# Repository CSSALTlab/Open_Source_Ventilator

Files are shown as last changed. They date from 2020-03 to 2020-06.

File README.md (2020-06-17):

# Open_Source_Ventilator
Open source for use worldwide and contributions from others worldwide

See out documentation at [https://cssaltlab.github.io/Open_Source_Ventilator/](https://cssaltlab.github.io/Open_Source_Ventilator/)

NOTE:
The ventilator code makes references to 2 outside libraries not included in the code found on Github or in the Arduino IDE.

These two libraries are:  

    AllSensors_DLHR (https://github.com/jeremycole/AllSensors_DLHR)
    BMP280 sensor library (https://itbrainpower.net/downloadables/sSense-BMx280.zip)

To add these two libraries to your Arduino IDE:

    Open your Arduino IDE
    Select "Sketch"->"Include Library"->"Add .ZIP library..."
    Navigate to the location of the .zip of the library you downloaded from the websites listed above

Do this for each of the two libraries needed.

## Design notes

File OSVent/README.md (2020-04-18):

# osventproto
OSVent Controller prototype

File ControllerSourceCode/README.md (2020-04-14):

# Controller Source Code Projects

* **ArduinoVent** The final target code for the Ventilator Controller

* **VentSim** The VentSim purpose is to focus on UI and high level control of the Ventilator. Some particular files will be port to the real Ventilator project and others emulates the native Arduino libraries.

### Very first Prototype (before CSSALT PBC)
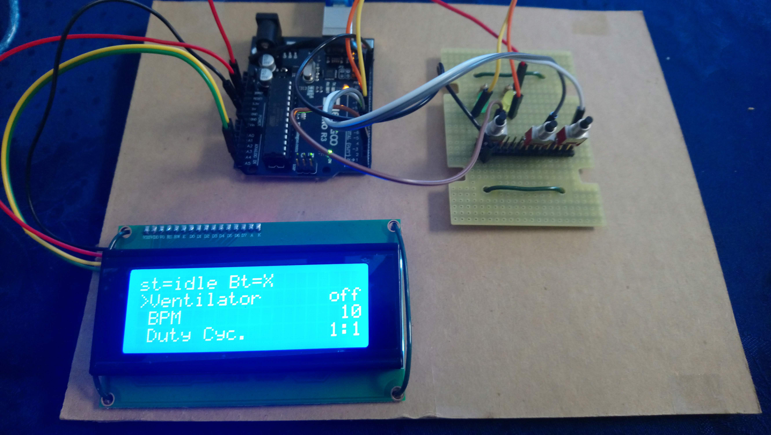
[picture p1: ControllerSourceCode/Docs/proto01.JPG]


### CSSALT PCB Schematic (thanks to Ashhar):
[Click here to see the schematic](Docs/schematic.pdf)

### Demos and Tutorials Videos
[click here for playlist with demo videos and tutorials](https://www.youtube.com/watch?v=gKr-EH8vHxM&list=PLtBsFN3o4c54h5fr7lDnGuZhvKIA5Fhd3)

## Controller
Main function: Provides control for inhalation/exhalation valves and/or stepper motor; monitors pressure and tidal volume. alarms in case of unexpected parameters (unexpected pressure, A/C power down, reset and etc). UI operated by LCD (20x4 20X2 or 16x2) and 3 buttons. Main settings: BPM, duty-cycle, pressure and tidal volume threshoulds.

## UI Options
Whoever is producing the Ventilator can opt to use LCD's: 16X2, 20X2 or 20X4. Interface can be I2C or Parallel. 
## UI Initial concept/proposal

### LCD/Buttons Interface
VentSim simulates the LCD and buttons. The LCD displays the following rows:

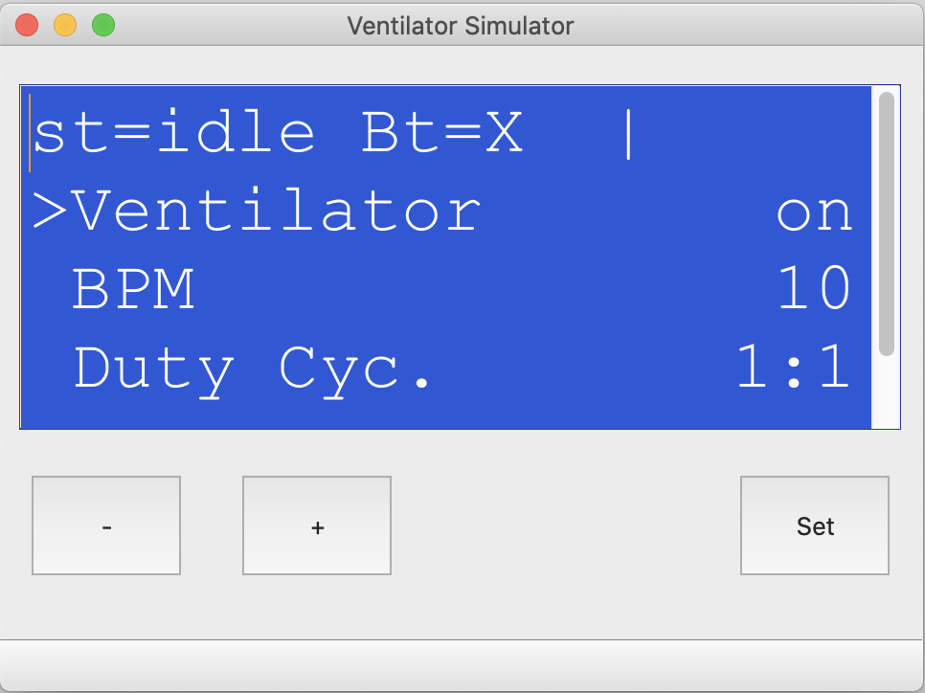
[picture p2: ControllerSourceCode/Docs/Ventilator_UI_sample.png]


Where the rows represent the following tokes:

 * **First Row**: St (Idle, On, or Error). 
   The last 6 characters on the right displays the breath progress, where "||||||" means lung full and 6 spaces empty lung. 

 * **The other rows** are scrollable and show parameters. In "Normal" mode the **"-"** and **"+"** buttons are use to scroll the parameter list. Pressing and hold the **"-"** button scrolls the list up to the top.
 To change a parameter the user needs to press and hold the **"Set"** button for half+ second; it enters in "Enter" mode; then the selected row starts flashing indicating that the parameter can be changed; the The **"-"** and **"+"** buttons increment or decrement the value; Pressing the **"Set"** button commits the change (and so if times-out) and return the unit to "Normal" mode. 

### To Do List
Click [here](TODO.md) to access the TODO list

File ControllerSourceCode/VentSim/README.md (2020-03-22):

# VentSim
The VentSim purpose is to focus on UI and high level control of the Ventilator. Some particular files will be port to the real Ventilator project and others emulates the native Arduino libraries.

## Project concept
The goal of the Ventilator project is to provide ways to anyone produce a ventilator using low cost out-of-shelf components.

### Some suggested components:

* Microcontroller (US$12)
[Amazon link](https://www.amazon.com/Emakefun-Development-Interface-Wireless-ATmega328P/dp/B07RDH8D4T/ref=sxin_0_ac_d_pm?ac_md=1-0-VW5kZXIgJDIw-ac_d_pm&cv_ct_cx=arduino+uno&keywords=arduino+uno&pd_rd_i=B07RDH8D4T&pd_rd_r=054f0126-5538-4fb4-93cc-5a2cf8431b4f&pd_rd_w=xVhNs&pd_rd_wg=rsURv&pf_rd_p=0e223c60-bcf8-4663-98f3-da892fbd4372&pf_rd_r=43RDPGY99Y567EFNAMYY&psc=1&qid=1584833975)
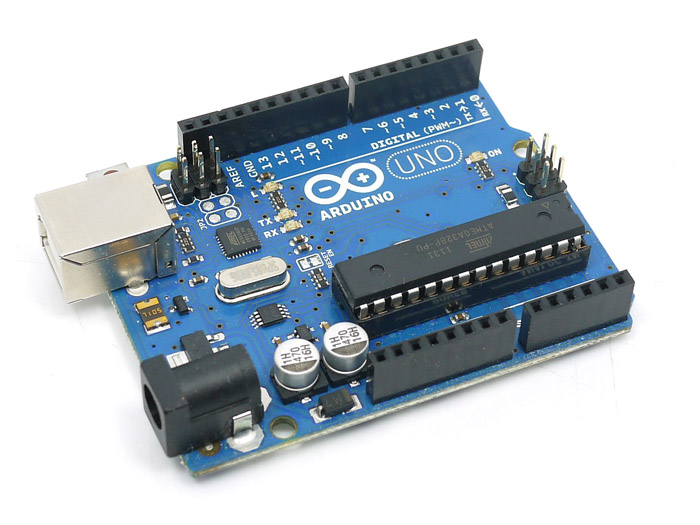
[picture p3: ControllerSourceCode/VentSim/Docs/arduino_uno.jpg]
Arduino


* LCD Module (US$12)
[Amazon link](https://www.amazon.com/ZealMax-Module-Interfaz-Arduino-MEGA2560/dp/B08181VP31/ref=sr_1_fkmr2_1?keywords=arduino+lcd+4+rows&qid=1584834089&sr=8-1-fkmr2)
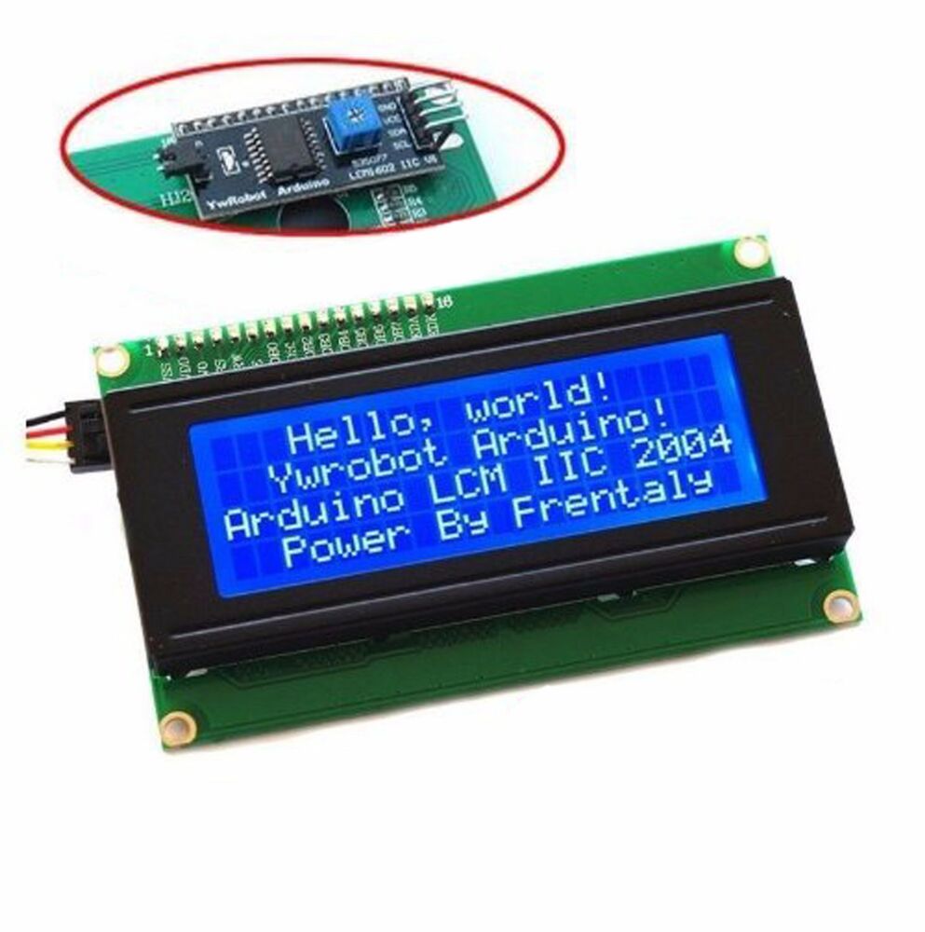
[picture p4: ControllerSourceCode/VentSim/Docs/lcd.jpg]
LCD


* BLE Module - (US$10)
[Amazon link](https://www.amazon.com/DSD-TECH-Bluetooth-iBeacon-Arduino/dp/B06WGZB2N4/ref=redir_mobile_desktop?ie=UTF8&aaxitk=SHdRdFy9Ybn2qMCGps1Sww&hsa_cr_id=8435439580201&ref_=sb_s_sparkle)
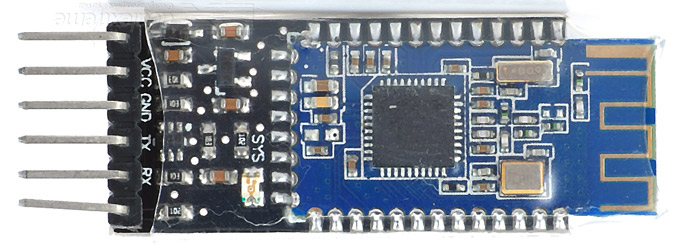
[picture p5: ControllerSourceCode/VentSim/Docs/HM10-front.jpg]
BLE


## Controller
At this point the team building the Ventilator only needs a timer to control breath rate via two valves: inhalation/exhalation valves. Later on we will add a step motor to drive a machanism to squeese a rubber bad/bottle in order to provide positive pressure.

## UI Options
Whoever is producing the Ventilator can opt to use either a LCD + 4 Buttons physical interface or an Android device connected via Bluetooth-LE (according to their budged and components availability). Both option can also coexist fine.

## UI Initial concept/proposal

### LCD/Buttons Interface
VentSim simulates the LCD and buttons. The LCD displays the following rows:

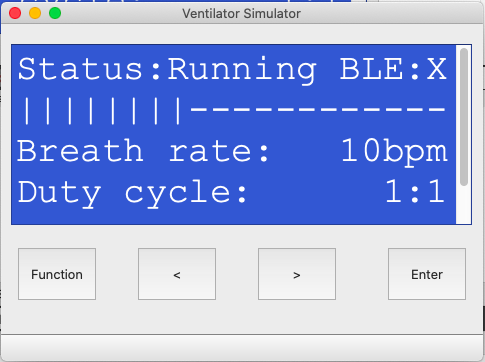
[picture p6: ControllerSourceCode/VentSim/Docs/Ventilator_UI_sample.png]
UI


Where the rows represent the following tokes:

 * **First**: Status (Idle, Alarm/Error or Running). BLE indicates:
   * X: Bluetooth is not installed
   * A: Bluettooth is disabled
   * A: Bluettooth is advertising
   * C: Bluettooth is connected.

 * **Second** row shows in real time the inhalation/exhalation progress.

 * **The other** rows are scrollable and show parameters. The operator can change the parameter values by pressing the Function button. The selected row starts flashing indicating that the parameter can be changed; If Function button is pressed once again then the next row will be selected (flash); if the arrows buttons are pressed then it will increase/decrease the parameter value. The Enter button will commit the change. If Enter button is not pressed (and no other button so) then it will time out and the current parameter will not be changed.

### Android UI
TBD

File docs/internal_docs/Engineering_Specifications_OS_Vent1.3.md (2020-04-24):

**Open Source Ventilator to Address Actual/Predicted Ventilator Shortage Worldwide due to COVID19 Pandemic – Distribute Freely**

V1.3 – Sem Lampotang; March 19, 2020, Department of Anesthesiology, Center for Safety, Simulation &amp; Advanced Learning Technologies, University of Florida, Gainesville, Florida, USA

**Engineering Design Specifications**

**Overall design philosophy**

- Open source for use worldwide and contributions from others worldwide
- Adult ventilator (older adults at higher risk)
- Positive pressure volume control ventilation
- Intubated patient
- A bare bones, safe design is better than nothing and what &quot;nothing&quot; means ….
- The supplies and materials will be locally available at hardware stores
- The design(s) will be validated; validation will be documented and transparent; as an academic research lab, CSSALT can do some of the verification and validation
- The design(s) will be modular allowing different modules to be mixed and matched depending on local availability
- Dissemination via Internet [https://simulation.health.ufl.edu/technology-development/open-source-ventilator-project/](https://simulation.health.ufl.edu/technology-development/open-source-ventilator-project/) and GitHub([https://github.com/CSSALTlab/Open\_Source\_Ventilator.git](https://github.com/CSSALTlab/Open_Source_Ventilator.git))

**Assumptions:**

1. FDA will waive clearance for the bare bones design if there is a massive shortage
2. Traditional medical components and supplies used in ventilators will be in short supply
3. Transportation will be impaired/disrupted. Locally available non-medical supplies and equipment readily available at local hardware stores such as sprinkler valves and PVC tubing will be used

**Ventilator Specifications:**

| | **Range** | **Accuracy** | **Settings** |
| --- | --- | --- | --- |
| **Volume Controlled Intermittent Mechanical Ventilation** |
| Tidal volume | 145-800 ml | ± 20% | Increments of 50 ml |
| Respiratory rate | 10 – 30 bpm | ± 2 bpm | 5 fixed settings: 10, 15, 20, 25, 30 bpm |
| I:E ratio; no inspiratory pause | 1:1 or 1:2 |-| 2 fixed settings |
| PEEP | 0 – 30 cm H2O;Default setting 16 cm H2O | ± 1 cm H2O | Adjustable or fixed settings depending on design |
| Air and O2 supplied at 50 ± 5 psig (345 kPa) |
| FiO2 | 0.21 – 1.0 | ± 0.05 | 3 fixed FiO2 settings: 0.21, 0.5, 1.0 |
| Anti-asphyxia valve | Opens at –3 ± 1 cm H2O |
| Over-Pressure Valve | Opens at 30 cm H2O ± 5 cm H2O |
| **Optional** |
| Spontaneous breathing |
| Weaning |
| In-built blender | 0.5 FiO2 |
| Oxygen sensor | 0.21 – 1.0 FiO2 | ± 0.05 FiO2 |

**Modules:**

Pneumatics

Inspiratory valve

Exhalation valve

PEEP valve

Pressure Regulation (optional)

3D print

Body

Accessories

Electronics

Printed circuit board

Microcontroller

Software or Timing circuit

Power Supply

12V DC preferred

User Interface

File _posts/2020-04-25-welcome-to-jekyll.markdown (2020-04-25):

---
layout: post
title:  "Welcome to Jekyll!"
date:   2020-04-25 01:56:21 -0400
categories: jekyll update
---
You’ll find this post in your `_posts` directory. Go ahead and edit it and re-build the site to see your changes. You can rebuild the site in many different ways, but the most common way is to run `jekyll serve`, which launches a web server and auto-regenerates your site when a file is updated.

Jekyll requires blog post files to be named according to the following format:

`YEAR-MONTH-DAY-title.MARKUP`

Where `YEAR` is a four-digit number, `MONTH` and `DAY` are both two-digit numbers, and `MARKUP` is the file extension representing the format used in the file. After that, include the necessary front matter. Take a look at the source for this post to get an idea about how it works.

Jekyll also offers powerful support for code snippets:

{% highlight ruby %}
def print_hi(name)
  puts "Hi, #{name}"
end
print_hi('Tom')
#=> prints 'Hi, Tom' to STDOUT.
{% endhighlight %}

Check out the [Jekyll docs][jekyll-docs] for more info on how to get the most out of Jekyll. File all bugs/feature requests at [Jekyll’s GitHub repo][jekyll-gh]. If you have questions, you can ask them on [Jekyll Talk][jekyll-talk].

[jekyll-docs]: https://jekyllrb.com/docs/home
[jekyll-gh]:   https://github.com/jekyll/jekyll
[jekyll-talk]: https://talk.jekyllrb.com/

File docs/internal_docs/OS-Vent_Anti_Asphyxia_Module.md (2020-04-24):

**Open Source Ventilator**

**Anti-Asphyxia Module**

V1.0; Sem Lampotang, March 18, 2020; Department of Anesthesiology, Center for Safety, Simulation &amp; Advanced Learning Technologies, University of Florida, Gainesville, Florida, USA

In an intubated patient, the patient will not be able to draw in a breath in periods other than the times during which mechanical inspiration occurs or if the gas supply fails, among others, that is 2/3 of the time if we use an inspiratory to expiratory time ratio of 1:2. An anti-asphyxia valve is a valve that opens when there is sub-ambient (below atmospheric pressure) pressure in the breathing circuit from the patient trying to breathe and not receiving gas. Anti-asphyxia valves typically crack open when the pressure in the breathing circuit is 3 cm H2O below atmospheric pressure. The anti-asphyxia valve module is placed using a T-connection in pneumatic connection with the patient.

| **Physical Input** | **Data/Control Input** | **Physical Output** | **Status** |
| --- | --- | --- | --- |
| **Design** Pressure in breathing circuit | Open the anti-asphyxia valve when breathing circuit pressure drops below -3 ± 1 cm H2O. Accuracy of ± 1 cm H2O | Room air is pulled by the patient via the anti-asphyxia valve as long as the breathing circuit pressure is below – 3 cm H2O Resistance to flow must be minimal. When open, resistance to flow through anti-asphyxia valve must be low (≤ 3 cm H2O/l/s) Design and build/3D print the anti-asphyxia valve and verify it is accurate within ± 1 cm H2O | Not claimed; No one working on it yet |
|
|||| Not claimed; No one working on it yet |

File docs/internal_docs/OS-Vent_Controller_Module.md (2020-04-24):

**Open Source Ventilator**

Controller Module

V1.0; Sem Lampotang, March 17, 2020; Department of Anesthesiology, Center for Safety, Simulation &amp; Advanced Learning Technologies, University of Florida, Gainesville, Florida, USA

This module is essentially a timer that turns two valves on or off. When the inspiratory valve is open, the exhalation valve is closed and vice versa.

Respiratory rate (RR) = Number of breaths per minute (bpm)

Breath duration = 60 s/RR; e.g., for 10 bpm, breath duration = 60/10 = 6 s

Inspiratory:Expiratory time ratio (I:E ratio) = 1:2 (usually)

Inspiratory time (Ti; time in seconds spent in inspiration phase) = breath duration / (1 + I:E) = 6/(1+2) = 6/3 = 2 seconds

Expiratory time (Te; time in seconds spent in exhalation phase) = breath duration – inspiratory time = 6 - 2 = = 4 seconds

Tidal volume (VT) = volume of gas (ml) delivered during inspiration

For a constant flow inspiration, the flow rate to the patient is VT/(inspiratory time)

| **Input** | **Data Output** | **Physical output** | **Status** |
| --- | --- | --- | --- |
| User selects tidal volume (see General Engineering Specifications) || Gas flows towards patient during the selected inspiratory time |
||| In constant flow design, gas flows to patient at a flow rate of VT/ |
 |
| User selects respiratory rate (see General Engineering Specifications) | Time when inspiration starts and ends | Time when gas starts flowing to patient Time when gas stops flowing to patient | Not claimed; No one working on it yet
|| Time when exhalation starts and ends | Time when gas starts flowing from patient Time when gas stops flowing from patient | No one working on it yet ; No one working on it yet |
| **Electromechanical design (no software)** |
| User selects respiratory rate (see General Engineering Specifications) | Time when inspiration starts and ends | 12 V delivered to inspiratory valve 0 V to exhalation valve | No one working on it yet ; No one working on it yet |
|
 | Time when exhalation starts and ends | 12 V delivered to exhalation valve0 V to inspiratory valve | No one working on it yet ; No one working on it yet |
|
| **Electromechanical design (software)** |
| User selection for tidal volume and respiratory rate (see General Engineering Specifications) | Variable &quot;INSPIRATORY\_VALVE\_ON&quot; is true when inspiration starts&quot;INSPIRATORY\_VALVE\_ON&quot; is false when inspiration end | 12 V delivered to inspiratory valve 0 V to exhalation valve | No one working on it yet ; No one working on it yet |
|
 || Variable &quot;EXHALATION\_VALVE\_ON&quot; is true when exhalation starts&quot;EXHALATION\_VALVE\_ON&quot; is false when exhalation ends | 12 V delivered to exhalation valve0 V to inspiratory valve | No one working on it yet ; No one working on it yet |
| **Pneumatic Design – May require specialized parts that may be out of stock** |

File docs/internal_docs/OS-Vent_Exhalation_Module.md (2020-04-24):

**Open Source Ventilator**

**Exhalation Module**

V1.0; Sem Lampotang, March 17, 2020; Department of Anesthesiology, Center for Safety, Simulation &amp; Advanced Learning Technologies, University of Florida, Gainesville, Florida, USA

The exhalation valve is closed when inspiration occurs so that gas from the inspiration module flows to the patient&#39;s lungs. The exhalation valve opens to allow the patient to exhale.

| **Physical Input** | **Data/Control Input** | **Physical Output** | **Status** |
| --- | --- | --- | --- |
| **Design A (balloon exhalation valve with solenoid-activated pilot valve)** |
 Exhaled gas from patient | Time exhalation valve should be open Time exhalation should be closed | Exhaled gas from patient. Inlet and outlet to exhalation module must accept 22 mm corrugated hose used in breathing circuit. When open, resistance to flow through exhalation valve must be low (≤ 3 cm H2O/l/s) | Not claimed; No one working on it yet |
|
| **Design B (exhalation valve with solenoid-activated gate or disc)**
Exhaled gas from patient | Time exhalation valve should be open Time exhalation should be closed | Exhaled gas from patient | Inlet and outlet to exhalation module must accept 22 mm corrugated hose used in breathing circuit When open, resistance to flow through exhalation valve must be low (≤ 3 cm H2O/l/s) | Not claimed; No one working on it yet |
| **Other?** |

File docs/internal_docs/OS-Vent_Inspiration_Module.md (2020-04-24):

**Open Source Ventilator**

**Inspiration Module**

V1.0; Sem Lampotang, March 17, 2020; Department of Anesthesiology, Center for Safety, Simulation &amp; Advanced Learning Technologies, University of Florida, Gainesville, Florida, USA

The inspiration module delivers gas to the patient during the inspiratory time Ti. The inspiration valve closes during exhalation.

| **Physical Input** | **Data/Control Input** | **Physical Output** | **Status** |
| --- | --- | --- | --- |
| **Design A (100% O2)** Oxygen at 50 ± 5 psig (345± 35 kPa) | Time inspiration should be on Time inspiration should be off | O2 flows towards patient at a given flow rate during the selected inspiratory time to deliver the desired tidal volume In a constant flow inspiration, the flow rate is VT/Ti l/s | Not claimed; No one working on it yet |
|
| **Design B (21%-100% O2)** Oxygen at 50 ± 5 psig (345± 35 kPa)Air at 50 ± 5 psig (345± 35 kPa) | FiO2 level selected by user Time inspiration should be on Time inspiration should be off | Gas at desired FiO2 flows towards patient at a given flow rate during the selected inspiratory time to deliver the desired tidal volume In a constant flow inspiration, the flow rate is VT/Ti l/s |
 |
| **Design C (room air)****Mechanically actuated self-inflating bag (aka &quot;Ambu&quot; bag)** | Time inspiration should be on Time inspiration should be off | Air flows towards patient during the selected inspiratory time to deliver the desired tidal volume | **URLs** |

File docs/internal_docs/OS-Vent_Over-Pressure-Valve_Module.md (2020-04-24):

**Open Source Ventilator**

**Over-Pressure Valve Module**

V1.0; Sem Lampotang, March 18, 2020; Department of Anesthesiology, Center for Safety, Simulation &amp; Advanced Learning Technologies, University of Florida, Gainesville, Florida, USA

In an intubated patient under positive pressure ventilation, a concern is that the breathing circuit pressure for some reason such as mechanical malfunction becomes much too high. An over-pressure valve is a cut-off that opens to release gas and therefore reduce breathing circuit pressure if the exceeds a threshold pressure limit. Over-pressure valve valves typically open when the pressure in the breathing circuit exceeds 60 cm H2O above atmospheric pressure. The design could have an adjustable (optional) over-pressure threshold with a default setting of 60 cm H2O. The over-pressure valve module is placed using a T-connection in pneumatic connection with the patient.

| **Physical Input** | **Data/Control Input** | **Physical Output** | **Status** |
| --- | --- | --- | --- |
| **Design** Pressure in breathing circuit | Open the over-pressure valve when breathing circuit pressure goes above -60 cm H2O ± 5 cm H2O. Accuracy of ± 5 cm H2O | Gas in the breathing circuit is released via the over-pressure valve as long as the breathing circuit pressure is above 60 cm H2O ± 5 cm H2O Resistance to flow must be minimal. When open, resistance to flow through over-pressure valve must be low (≤ 3 cm H2O/l/s) Design and build/3D print the over-pressure valve and verify it is accurate within ± 5 cm H2O | Not claimed; No one working on it yet |
|

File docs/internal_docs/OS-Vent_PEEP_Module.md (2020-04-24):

**Open Source Ventilator**

**PEEP (Positive End Expiratory Pressure) Module**

V1.0; Sem Lampotang, March 17, 2020; Department of Anesthesiology, Center for Safety, Simulation &amp; Advanced Learning Technologies, University of Florida, Gainesville, Florida, USA

Reports from our clinical colleagues treating COVID19 patients indicate that PEEP is needed. A patient usually exhales to atmospheric pressure during positive pressure ventilation. Positive pressure means pressure above atmospheric pressure. Simply put, a PEEP valve stops the flow of exhaled gas when the pressure at the end of expiration is at the desired positive pressure.

| **Physical Input** | **Data/Control Input** | **Physical Output** | **Status** |
| --- | --- | --- | --- |
| **Design A (water column)** Gas exhaled by the patient coming from the exhalation valve | Close the PEEP valve when pressure drops below PEEP. Place the end of a 22 mm hose x cm below a translucent plastic cylinder of water with cm markings on the side of the cylinder | Gas exhaled by the patient as long as pressure is above the PEEP level The depth x in cm of the hose end below the water should be the PEEP level in cm H2O Design and build/3D print the PEEP column and verify it is accurate within ±1 cm H2O | Not claimed; No one working on it yet |
|
| **Design B (Spring-loaded valve)** Gas exhaled by the patient coming from the exhalation valve | Inlet port to PEEP valve is 22 mm corrugated hose Close the PEEP valve when pressure drops below PEEP | Gas exhaled by the patient as long as pressure is above the PEEP level Discrete PEEP valves for each PEEP level based on spring tension or an adjustable spring tension for different PEEP levels Design and build/3D print the PEEP column and verify it is accurate within 1 cm H2O | Not claimed; No one working on it yet |

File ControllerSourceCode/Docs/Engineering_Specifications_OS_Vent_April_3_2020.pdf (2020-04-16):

Open Source Ventilator to Address Actual/Predicted Ventilator Shortage Worldwide due to COVID19 Pandemic – Distribute Freely

V1.6 – Sem Lampotang, Dave Lizdas, Tony Destephens, Ilana Zarour; April 3, 2020, Department of Anesthesiology, Center for Safety, Simulation & Advanced Learning Technologies, University of Florida, Gainesville, Florida, USA

Engineering Design Specifications (preliminary and subject to change as needed to meet end-user needs)

Overall design philosophy

- Open source for use worldwide and contributions from others worldwide
- Adult ventilator (older adults at higher risk)
- Positive pressure volume control ventilation for intubated patients who are not spontaneously breathing
- A bare bones, safe design is better than nothing and what “nothing” means ….
- The design(s) will be validated; validation will be documented and transparent; as an academic research lab, CSSALT can do some of the verification and validation
- The design(s) will be modular allowing different modules to be mixed and matched depending on local availability
- Unboxed design – all parts directly accessible
- Design will be inexpensive to build (parts for base model less than $300 US) and assembled quickly (less than TBD hours) with readily accessible parts
- Dissemination via Internet https://simulation.health.ufl.edu/technology-development/open-source-ventilator-project/ (https://simulation.health.ufl.edu/technology-development/open-source-ventilator-project/) and GitHub(https://github.com/CSSALTlab/Open_Source_Ventilator.git)

Assumptions:

1. FDA will waive clearance for the bare bones design if there is a massive shortage
2. Traditional medical components and supplies used in ventilators will be in short supply
3. Transportation will be impaired/disrupted. Locally available non-medical supplies and equipment readily available at local hardware stores such as sprinkler valves and PVC tubing will be used

Ventilator Specifications:

| Range | Accuracy | Settings
Volume Controlled Intermittent Mechanical Ventilation
Tidal volume (TV) | 250-800 ml | ± 25 ml | Increments of 50 ml
Respiratory rate (RR) | 10 – 30 bpm | ± 0.5 bpm | Increments of 2
I:E ratio | 1:1 or 1:2 (1:3 optional) | - | 2 fixed and 1 optional setting
PEEP valve | 5 – 25 cm H2O; Default setting 5 cm H2O | ± 1 cm H2O | Can either be adjustable in 5 cmH2O increments or continuously adjustable

Air and O2 supplied at 50 ± 5 psig (345 kPa)

FiO2 | 0.21 or 1.0
Anti-asphyxia valve | Opens at –3 cmH2O | ± 1 cm H2O
Over-Pressure Valve | Opens at 40 default, adjust up to 60- cmH2O | ± 5 cm H2O | Manually controlled

Optional
Plateau pressure | Limited to 35 cmH2O | | Controlled in software
Peak pressure | < 2cmH2O + Plateau | | Controlled in software
Inspiratory pause | 25% inspiratory time | -
Spontaneous breathing | | | Ventilation mode
In-built blender | 0.21 – 1.0 FiO2 | ± 0.05 (+/- 5%) | 3 fixed FiO2 settings: 0.21, 0.5, 1.0 Variable between 30% and 100% in 10% steps preferred
Oxygen sensor | 0.21 – 1.0 FiO2 | ± 0.05 FiO2

Sensors (optional – not in base design):

Airway pressure sensor

- Connected at 22mm inspiratory port connection
- Capable of measurement ranges of -20 cmH2O to 60 cmH2O (rated for 120 cmH2O over-pressurization)
- at least 1.0 cmH2O resolution
- Used for:
- disconnect and overpressure alarms
- displaying PEEP, peak and plateau airway pressure with waveform (waveform optional)
- aborting inspiration if High inspiratory airway pressure reached

Flow Sensor

- Connected at expiratory port
- Capable of measurement during maximum conditions: max TV 800 ml, RR 30, IE 1:2
- Max flowrate at least 1200 mL/s (72 LPM)
- Accuracy +/- 40 mL/s
- Max flow resistance 2.2 cmH2O at 60 LPM
- Used for:
- Measuring TV via integration over time (measured TV accurate to +/- 25 ml nominal, ideally +/- 10 ml)
- Low/High TV alarms
- Must be able to withstand airway pressures (rated for 120 cmH2O over-pressurization)

User Interface:

− Display
- 20x4 LCD display or equivalent for base design, non-base design supports touchscreen
- Capable of continuously displaying:
User settings for TV, RR, I:E
Ventilator output for TV, PEEP, airway pressure (Paw)
Optional (FiO2, ventilation mode, EtCO2, ventilator output for RR) Alarms
− Adjustable variables
- RR,
- I:E,
- TV,
- Alarm limits

Alarms:

− Patient Disconnect
- Condition: pressure does not rise above 3 cmH2O during inspiration
- Audible alarm and UI text “LOW AIRWAY PRESSURE” [16 Char: LOW AIRWAY PRES! (16 characters)] − High inspiratory airway pressure
- Condition: airway pressure above alarm setting during inspiration
- Adjustable range: 15- 60 cmH2O, increments of 5 cmH2O
- Default setting: 35 cmH2O
- Audible alarm and UI text “OVER-PRESSURE ALARM” [16 char: OVER PRES ALARM! (16 characters)]
- Controller feedback:
Inspiratory solenoid valve closes to stop inspiratory flow Exhalation valve opens (if controlled by solenoid)
− TV High/Low
- Adjustable range: 200-1000 ml, increments of 50 ml
- Default low alarm setting: 200 ml; Default high alarm setting: 1000 ml
- Audible alarm and UI text:
“TV HIGH” Condition: measured TV exceeds high TV alarm setting
“SET TV NOT DELIVERED” Condition: measured TV less than low TV alarm setting [16 Char: SET TV NOT DELIV]
“LOW VT, IT SHORTENED” Condition: Inspiration Time (IT) is shortened by reaching high inspiratory airway pressure limit and measured TV less than low TV alarm setting [16 Char: LOW VT/IT SHORT]
− MV (Minute ventilation) High/Low (Optional):
- Adjustable range: 2 L- 15 L, increments of 1 L
- Default low setting: 4 L; Default high setting: 8 L
- "MV HIGH” Condition: MV greater than high MV alarm setting
- “MV LOW” Condition: MV less than low MV alarm setting
− Gas pipeline failure (Optional)

- Condition: no supply pressure detected
- Audible alarm and UI text “GAS SUPPLY FAILURE” [16 Char: GAS SUPPLY FAIL! (16 char)] − Electricity supply failure (Optional)
- Condition: ventilator unplugged from wall mains
- Audible alarm and UI text “ELECTRIC SUPPLY FAIL” [16 Char: ELECT SUPP FAIL! (16 char)]
− Machine switched off when in mandatory ventilation mode ("Rapidly manufactured ventilator system specification", 2020)
- 16 Char: "VENT TURNED OFF!"
− If multiple alarms simultaneously present and display has one line of text for alarms, display line will toggle through all alarms at one second intervals

Incoming gas supply:

− Must connect to wall pipeline or gas blender
- Male Oxygen DISS connector (from hose)
− (Optional) All gas connectors and hoses must use standard non-interchangeable connectors and be color coded according to current standards ("Rapidly manufactured ventilator system specification", 2020).
- (Optional) Can incorporate a backup oxygen cylinder connected via either Schrader valve or Pin Index System ("Rapidly manufactured ventilator system specification", 2020).

Electrical supply:

− Ability to connect to 120-240V mains
− Must have 30 minutes backup battery in case of mains electricity failure
− Optionally hot swappable batteries so that it can be run on battery supply for an extended period, for example, 2 hours for within hospital transfer ("Rapidly manufactured ventilator system specification", 2020).
− Must avoid harmful RF or EM emissions that could interfere with other critical machinery ("Rapidly manufactured ventilator system specification", 2020).

Gas supply to patient:

Patient breathing system connections- the ventilator must present 22mm outside diameter (OD) ‘male’ standard connectors for connection to user supplied 22mm ‘female’ connectors on the breathing system ("Rapidly manufactured ventilator system specification", 2020).

All elements in the gas pathway must meet biological safety and oxygen safety standards, especially to minimize risk of fire or contamination of the patient’s airway ("Rapidly manufactured ventilator system specification", 2020).

Infection Control:

− All parts in contact with pathogens must be either disposable or able to be decontaminated between patients ("Rapidly manufactured ventilator system specification", 2020).
− All external surfaces must be cleanable in the likely event that they get respiratory secretions or blood splatter on them. Cleaning would be by healthcare workers manually wiping using an approved surface wipe with disinfectant or cloths and approved surface cleaning liquid ("Rapidly manufactured ventilator system specification", 2020).
− Ability to add in line, replaceable HEPA and HME filters to inspiratory circuit.

Miscellaneous:

− Exhalation valve flow resistance: no more than 1.5 cmH2O at 60LPM gas flow
− Over-Pressure Valve flow resistance: no more than 1.5 cmH2O at 60LPM gas flow
− Anti-asphyxia valve flow resistance: no more than 1.5 cmH2O at 60LPM gas flow
− Must be able to deliver 800ml TV 30BPM I:E 1:2 at a constant flow throughout entire inspiration cycle
− It must have 100% duty cycle (100% up time) for up to 14 days. Optionally it can be used beyond 14 days, the expected durability must be specified ("Rapidly manufactured ventilator system specification", 2020).
− Can be floor standing ("Rapidly manufactured ventilator system specification", 2020).
− Ideally small and light enough to mount on patient bed and orientation-independent functioning ("Rapidly manufactured ventilator system specification", 2020).
− Should be as robust as possible. For example, it may be dropped from bed height to floor ("Rapidly manufactured ventilator system specification", 2020).
− It must be intuitive to use for qualified medical personnel, but these may not be specialists in ventilator use ("Rapidly manufactured ventilator system specification", 2020):
- must not require more than 30 minutes training for a doctor with some experience of ventilator use ("Rapidly manufactured ventilator system specification", 2020)
- Must include instructions for use ("Rapidly manufactured ventilator system specification", 2020)
- Must have transparent design, supply chain, manufacture and testing processes that are of sufficient quality to enable regulatory officials to deem appropriate for usage in exceptional circumstances ("Rapidly manufactured ventilator system specification", 2020).
− Must not be excessively cumbersome so that it would impede hospital operations or prevent easy movement within hospital premises ("Rapidly manufactured ventilator system specification", 2020).
− Avoidance of hot spots (overheating components).

References:

Rapidly manufactured ventilator system specification. (2020, March 20). Retrieved March 24, 2020, from https://www.gov.uk/government/publications/coronavirus-covid-19-ventilator-supply-specification/rapidly-manufactured-ventilator-system-specification

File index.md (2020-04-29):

---
layout: default
title: Home
---
# About page

This page tells you a little bit about me.

This is the Open Source Ventilator Project from the University of Forida.

[Operator's manual](./docs/OperatorsManual/manual.md)

[Aeesmbly Instructions](./docs/electronics/assembly_instructions.html)

[version 1.0 testing report](./docs/tests/test_v1.html)

[version 1.09 testing report](./docs/tests/test_v109.html)

Developers:

  [Guide to adding / editing documentation](./docs/AddingDocumentation.md)

  [Guide to developing / testing](./docs/testing/developing_guide.html)

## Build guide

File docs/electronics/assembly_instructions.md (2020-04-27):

# Assembly Instructions
DRAFT V1.
Gordon L. Gibby MD KX4Z
Address questions to docvacuumtubes@gmail.com

|DATE| VERSION| Changes|
|---|---|---|
|4/15/20| Draft 1.0| Original Document|
|4/20/20| Draft 1.1 |Utilized Ashhar 1.0 Board|
|||Added wooden standoffs glued to Ashhar 1.0 Board|
|||Allows use of 4x20 display, but compatible with 2x16 code;|
|||with a different cut-out will accmodoate 2x16 display as well.|
|||Mounted Transducer board to front panel instead of to rear of main board|
|||Provided a Drill Template and dimensions.|
|||Provided a working list of TOOLS REQUIRED|
|4/20/20| Draft 1.2 |Added missing photo of the tools required.|
|4/21/20| Draft 1.3| Added wiring information for I2C bus connections to Transducer board|
|4/23/20| Draft 1.4| Details on final build of Prototype #2|
|4/24/20| Draft 1.5| Added overview wiring diagram|
|||Added R-numbers to Schematic, added missing R10 to list.|
|||Rewrote bill of materials for the electrical construction of the transducer board.|
|||Rescanned the schematic to improve quality.|
|||Listed “missing” resistors (not used)|

## Partial Mechanical Bill of Materials

|# |Item Description| Item sourcing suggested|
|--|--|--|
|1| Carlon 8”x8”x4” electrical box|Home Depot or equivalent https://www.homedepot.com/p/Carlon-8-in-x-4-in-PVC-Junction-Box-E989N-CAR/|
|2| Chosen LCD Display| Connection pins must be on the back of the board and must be long enough to properly connect to the socket on the main board.|
|||20x4: https://www.amazon.com/gp/product/B00GZ6GK7A/ref=ppx_yo_dt_b_asin_title_o08_s00?ie=UTF8&psc=|
|||https://www.amazon.com/gp/product/B071W8SW9R/ref=ppx_yo_dt_b_asin_title_o06_s00?ie=UTF8&psc=
|3 |Pushbuttons| https://www.amazon.com/gp/product/B0752RMB7Q/ref=ppx_yo_dt_b_asin_title_o09_s00?ie=UTF8&psc=|
|4| Pine dowels |3/8” outer diameter x 0.90” length, square cuts, pine (soft)Remember to make pilot drills before inserting sheet metal screws.|
|5| Sheet metal screws| #6 x 5/8” to secure the main board standoffs from the front –qty 3 required.|
|6| #16 or #18 stranded wire, both red and black colors required.|Power supply wiring|
|7| #22-#28 stranded wire| To wire the push buttons. Stranded wire from a Cat5 ethernet cable is excellent.|
|8| Solenoid output jack| CB microphone 4-pin secure insulated jack https://www.amazon.com/PIN-PANEL-MOUNT-MICROPHONE-CONNECTOR/dp/B00H579TXU|
|||Pin 1 = MOTOR_A|
|||Pin 2 = MOTOR_B|
|||Pin 3, 4 = GROUND|
|9| Solenoid plug| https://www.amazon.com/4-PIN-CB-MICROPHONE-PLUG/dp/B00H572J3W (CB microphone 4-pin plug)|
|10| Mean Well 15 volt medical grade power supply| https://www.digikey.com/product-detail/en/mean-well-usa-inc/GSM40B15-P1J/1866-2009-ND/|
|11| BMP or BME| Adafruit version:|
|||https://www.amazon.com/Adafruit-BME280-Temperature-Humidity-Pressure/dp/B013W1AJUY (I2C address 0x77 if not jumpers utilized)
|||An alternative Kee-Yee product has been successfully used but requires a different I2C address (0x76)|
|12| Airway tubing connectors| https://www.amazon.com/Swordfish-61120-Vacuum-Connector-Assortment/dp/B07HV8CVZ|
|13| I2C 3.3V differential pressure transducer, 200Pa| https://www.digikey.com/product-detail/en/amphenol-all-sensors-corporation/DLHR-F50D-E1BD-C-NAV8/442-1163-ND/
|14| PCB for I2C 3.3 V differential pressure transducer, 200 Pa|Manufacturer may redesign the Transducer/power supply board, or use standard perfboard for mounting.|
|15| Nylon insulated standoffs with M3 threads, screws and nuts, assorted lengths|Assortment: https://www.amazon.com/gp/product/B01HDR72Q2/ref=ppx_yo_dt_b_search_asin_title?ie=UTF8&psc=
||Barbed plastic airway tubing connectors |https://www.amazon.com/Swordfish-61120-Vacuum-Connector-Assortment/dp/B07HV8CVZ
||Optional Battery| DURA 12-3.3F Duracell 3.3 AGM 12V sealed lead battery.|
||20x4 Standoffs| M3 nylon standoffs 0392” from shoulder to flat side (Mthreaded screw portion is in addition to this size)|
||Transducer board Standoffs| M3 nylon standoffs 0.600” from shoulder to flat side, not including the threaded screw portion.|

### DRILL TEMPLATE (must be printed so that the lines are exactly 1” grid)
This photo would not fit on this page so it is shown at approximately 66% of normal size



#### NOTE FOR AIR PRESSURE CONNECTORS:

|---|---|
|If using small fuel tubing (approx 1/8” ID) the smallest size nipple (1/8”) in the specified vacuum fitting set will work.| Drill 0.160 for the 1/8” barbs from the specified kit|
|If using smaller tubing (e.g. for 2mm brass connectors)| Drill appropriately for the 2mm connectors.|
||If you have these – it is an advantage as the connections to the I2C differential pressure transducer work better with the 2mm tubing.
||If you don’t have them --- then use tubing to make “adapters” of short sections to go from small tubing to large tubing.|
||The final released versio to the hospitals should have 2mm connectors for the flow measurements, but we can fix that later.|

## Actual Assembly Instructions
### Micro Controller and Electrical Cabinet
1. **Use good engineering practice in all steps where there are issues and record any pertinent
discoveries or suggestions for improvement back to the CSSALT Team (Travis Johnson) @ UF.
Please note any errors in dimensions or conflicts and notify additionally
docvacuumtubes@gmail.com**
1. Choose either a common 16x2 or 20x4 LCD display of any desired color, as requested by
customer, without I2C connectors (we are using parallel wiring connections). The 20x4 is preferred.
The photos that follow are for a 20x4 build. See bill of materials above.
1. Choose an Arduino Nano with 328P processor or suitable backwards compatible improved
device with equal or greater RAM / EEPROM. (Program with supplied code from UF CSSALT)
1. Acquire the electrical plastic cabinet. 8”x8”x4” or larger. A suitable box is: Carlon
[https://www.homedepot.com/p/Carlon-8-in-x-4-in-PVC-Junction-Box-E989N-CAR/100404099](https://www.homedepot.com/p/Carlon-8-in-x-4-in-PVC-Junction-Box-E989N-CAR/100404099) (as per
Bill of Materials above)
1. If the customer requests built-in battery backup, procure a DURA 12-3.3F Duracell 3.3 AGM
12V sealed lead battery.

    This battery can be glued with Epoxy glue as follows, and **must be fully charged by an external
    power supply (suggested, Walmart Everstart 3A battery smart maintainer) before delivery** :

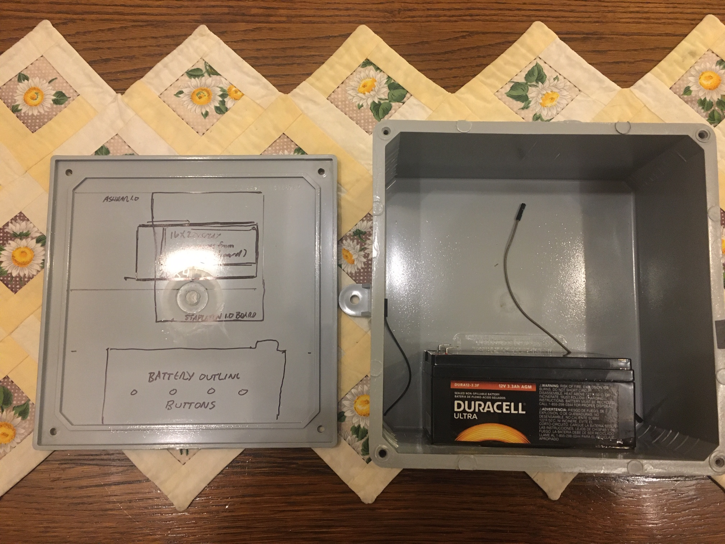
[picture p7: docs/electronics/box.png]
    

1. Assemble the Ashhar Farhan v. 1.0 Board. With the following adjustments:

    |#| Item| Comment|
    |1| BNC or RCA phono jacks NOT REQUIRED |You will likely prefer to utilize #18 or # stranded wire to connect to the “CB 4-pin microphone jack” INSTEAD OF THE BNC OR RCA PHONO JACKS|
    |||Pin 1 = output of MOTOR_A|
    |||Pin 2 = output of MOTOR_B|
    |||Pin3 , 4: GROUND|
    |||Jack body of 4-pin microphone jack – unconnected.|
    |||You may also utilize the appropriate BNC or RCA phono plug if you prefer to install the jacks, and wire to the CB 4-pin microphone jack. This is up to manufacturer preference.|
    |2 |298 Motor controller NOT REQUIRED| Not required. Please do not populate|
    |3| Relays NOT REQUIRED| Not required. Please do not populate|
    |4| Pushbuttons on Board NOT REQUIRED and best not to install | Not required – your assembly will be easier if you do not install them, because you need tosolder stranded wire to your choice of pushbuttons or membrane switches on the front panel.|
    |5| J8 TFT connector| NOT REQUIRED|

1. Orient the Ashhar 1.0 board horizontally well above the battery, note where the chosen display will
be located and **cut an opening for the display** , with approximately <1/16” gap. Later the gap will be
sealed with RTV or caulk. **See Drill Template attached,** and included above. – _print template in
such a magnification that the axes lines are exactly 1.00 inch if you are going to use it as a drill
template. (Note that the board is offset from all interior walls to allow for connectors if utilized )_
1. **_Prepare three pine dowels 3/8” diameter x 0.90” length, with square cuts._** Glue to the board at
the locations specified and be certain that they remain VERTICAL. Suggested to use JBWeld Clear
Epoxy, 5-minute epoxy glue. Place a tiny dab of epoxy on the upper face of the standoffs to harden
them.

    NOTE: that the 20x4 mounting holes do not match the 16x2 holes on the Ashhar 1.0 Board. Your
    board may be slightly different. Make minute changes as needed – the mounting holes for the
    BOARD (pine dowels) and the 20x4 DISPLAY, must agree with each other and depend on the exact
    dimensions of your 20x4 Display WITH THE PINS MATCHING THE PIN HOLES IN THE MAIN
    BOARD. The pins must reach the board pin-sockets when everything is mounted.

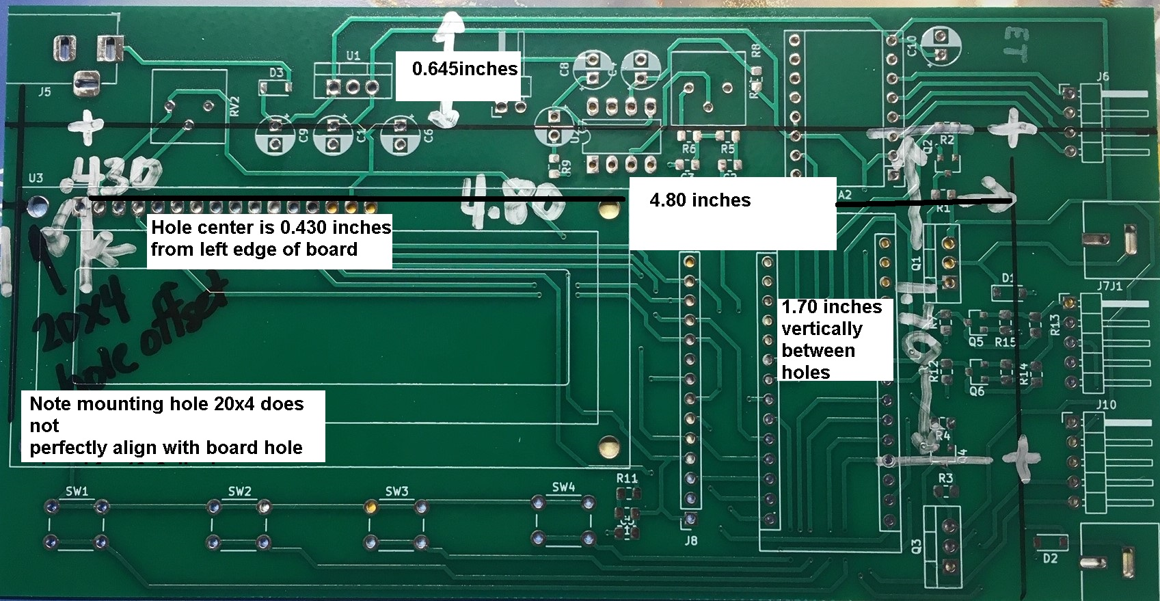
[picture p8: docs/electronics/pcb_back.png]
    

    Drawing of placement of Pin Standoff Dowels.

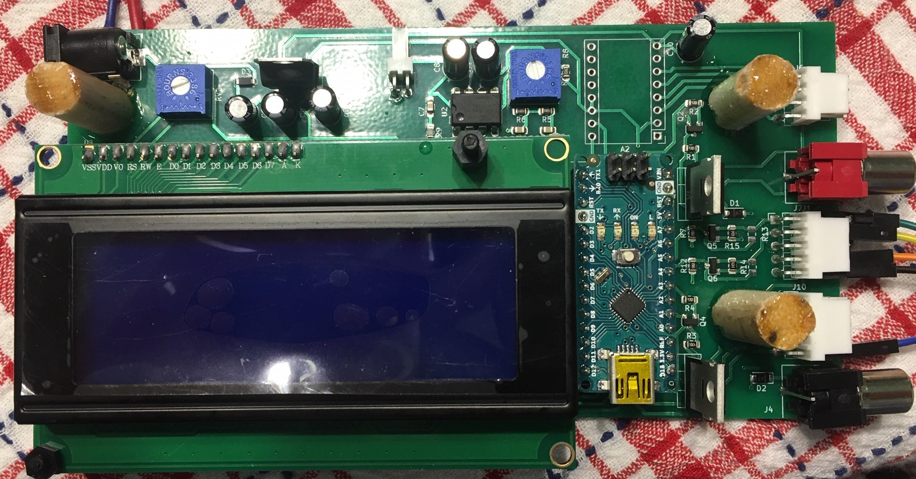
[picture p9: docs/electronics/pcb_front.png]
    

    Photo of example glued pine standoff dowels.

    Cut a hole for the chosen display following the template. It may be useful to use a 3/8” drill inside the
    corners, to allow a sabre saw (jig saw) to make the square cuts. Use a fine-toothed metal-cutting blade
    or equivalent, and go slowly.

    Either use numerically controlled drilling, careful measurements or simply affix the full size Drill
    Template to the inside of the Carlon box cover: (This is best done by spreading 5-minute Epoxy over
    the ENTIRE surface so the entire paper will be affixed and will not rip during drilling procedures.)

    

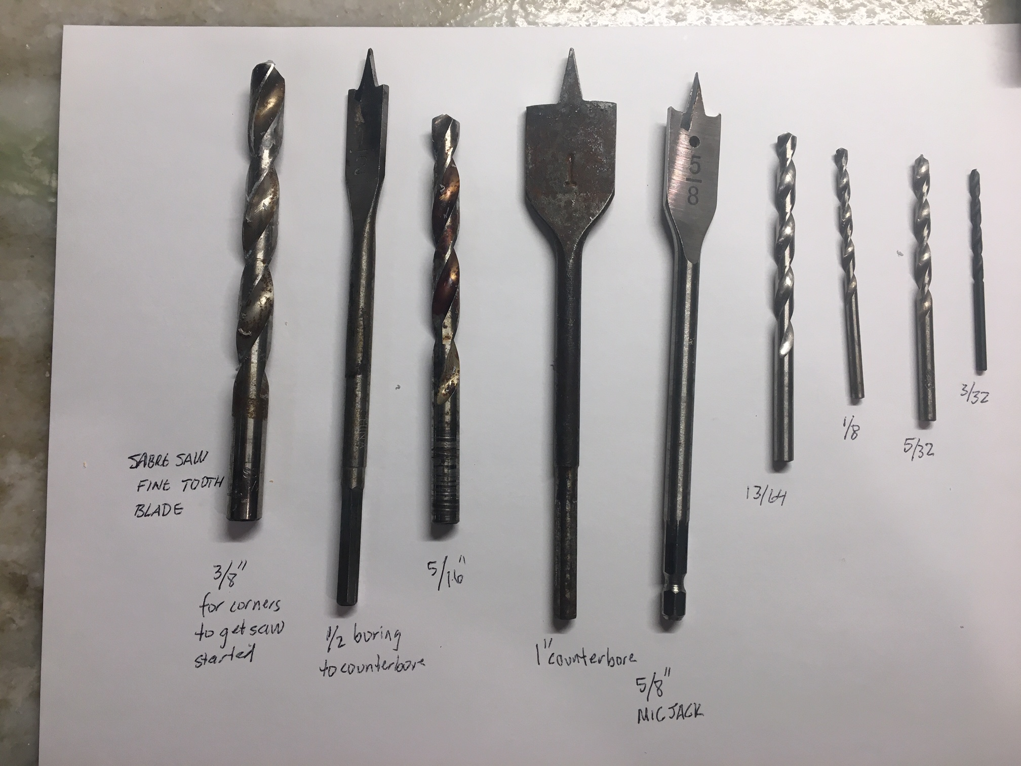
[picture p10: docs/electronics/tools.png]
    

    Photo of all the tools that I used:

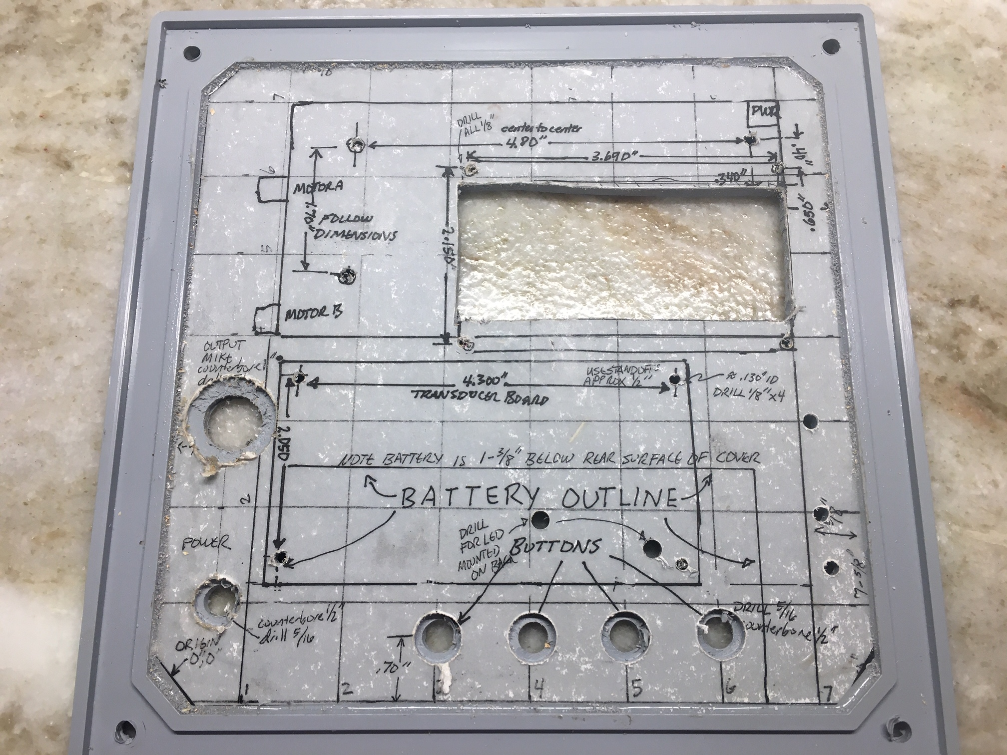
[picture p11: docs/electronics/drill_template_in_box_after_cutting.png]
    

1. Test Fit the chosen display and verify that the holes for its mounting standoffs are properly located – there can be some variation in the displays. Drill for M3 plastic screws using a 1/8” drill bit and
mount the LCD display with 0.392” STANDOFFS chosen such that the Board and Display will MATE
PROPERLY when both are mounted – 0.392” standoffs (not included the threaded screw portion, but
from shoulder to end) work well.

    Mount the 20x4 display; the front edge of the Display will be flush with the INNER surface of the top
    cover. After all is assembled, this gap will need to be filled with RTV.

1. Note that many devices, including many pushbuttons, will need to have a counter-bore of the thick
electric plastic box in order to allow the short threaded portion of the device to have adequate purchase
from its assembly nut to the device. This will apply to the _pushbuttons_ , the female _coaxial power
input_ , and the _4-pin microphone output jack_. The counterbores are done with a flat cutting wood
boring bit, 1/2” and 1” as noted in the drill template.

1. Mount an input power coaxial jack suitable for the plug on the output of the medical grade Mean
Well 15VDC power supply. Wire the coaxial power input jack using #16-#18 stranded wire (red for
positive black for negative) to the “17V” input of the Transducer Board, and to ground on the
transducer board. A 15-volt medical grade MEAN WELL power supply is required, but connects to the
17V input, not the 13.8-16V input. (eg. https://www.digikey.com/product-detail/en/mean-well-usa-inc/
GSM40B15-P1J/1866-2009-ND/7703561 )

    NOTE that the Mean Well medical grade power supply produces 15VDC – but on the transducer board,
    it connects its positive output to the “17V” input. This is purposeful. The resulting output is correct.

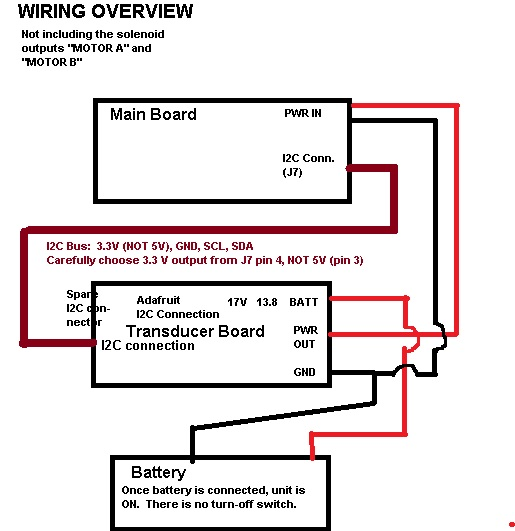
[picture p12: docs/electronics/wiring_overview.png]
    

1. The OUTPUT of the transducer board will need to be connected to the Main Board using #18-#
stranded wire, paying attention to POLARITY (center positive, outer negative) on the input power
coaxial jack. It is difficult to find a male plug to fit into the main board coaxial jack – you may solder
    to the correct solder points on the main board power input jack. Note that the main board includes a
    series diode for polarity protection.

### TRANSDUCER/POWER SUPPLY BOARD: BATTERY

1. If a battery is requested by the customer, wire the battery (positive and ground wires) using
female, insulated, crimp terminals to mate with the battery and #16–#18 stranded wire. Observe
polarity; diodes will prevent the battery from being utilized if it is connected backward, but the trickle
charging circuity may be damaged. Use RED for the positive wire and BLACK for the ground
connection (to MINUS on the battery)
1. **Solder the AC PWR LED ( GREEN ) and ON BATT LED (RED) to the BACK side of the
transducer board** , at an appropriate length so that they enter the holes drilled for them on the top
cover of the box, using the plastic standoffs.
1. Mount the ADAFRUIT BMP/BME280 breakout board (https://www.amazon.com/Adafruit-
BME280-Temperature-Humidity-Pressure/dp/B013W1AJUY or alternate supplier ) to the board with
soldered connections, and glue on the barbed nipple as per demonstration and information from David
Lizdas.

    BMP280 utilize one of the 1/4” x 1/8” adapters, (from a kit such as:
    [https://www.amazon.com/Swordfish-61120-Vacuum-Connector-Assortment/dp/B07HV8CVZ](https://www.amazon.com/Swordfish-61120-Vacuum-Connector-Assortment/dp/B07HV8CVZ)
    ) epoxy glue the 1/4” side AROUND the bmp280 to the board itself, being careful NOT to get
    glue inside on the BMP280 chip.

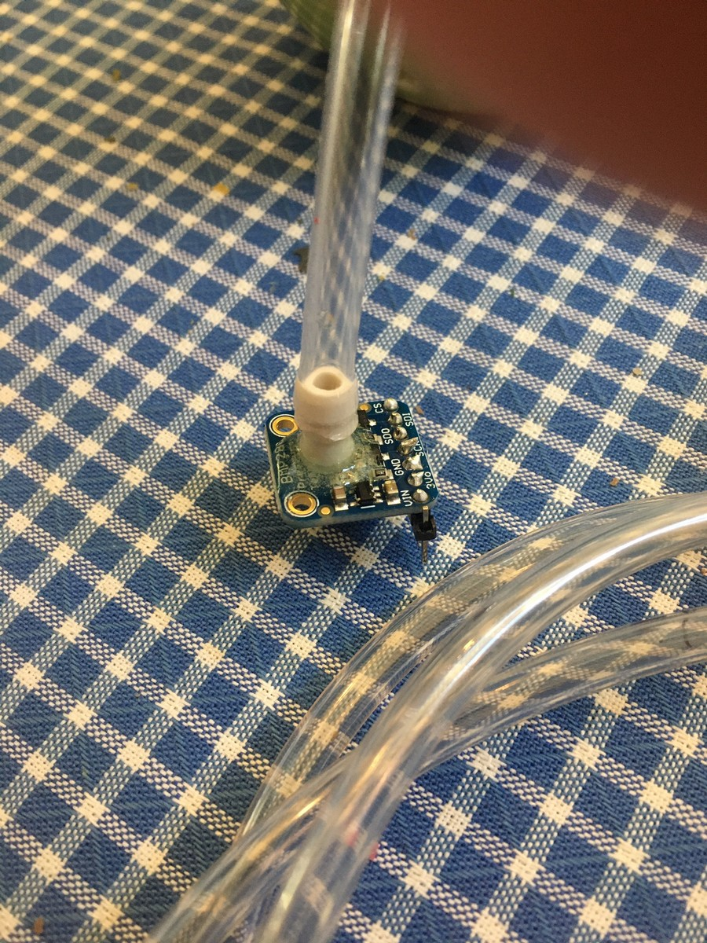
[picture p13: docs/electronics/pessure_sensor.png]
    

    (the 1/4” x 1/8” adapter barb is preferred to allow smaller tubing to be utilized )

1. Wire the chosen differential pressure transducer with a suitable glue onto the board; the traces on
the board **do not match the current choice for the differential pressure transducer, so it must be
individually wired to the ASHHAR 1.0 board using stranded wire (suggest size #22-#32).**

    The differential transducer part specified is: https://www.digikey.com/product-detail/en/amphenol-all-
    sensors-corporation/DLHR-F50D-E1BD-C-NAV8/442-1163-ND/6200354 Note that this is a 3.3 Volt
    maximum device I2C – do NOT connect to 5.0 V. **We unfortunately do not have a printed circuit
    board for this discrete part**. Manufacturer may optionally

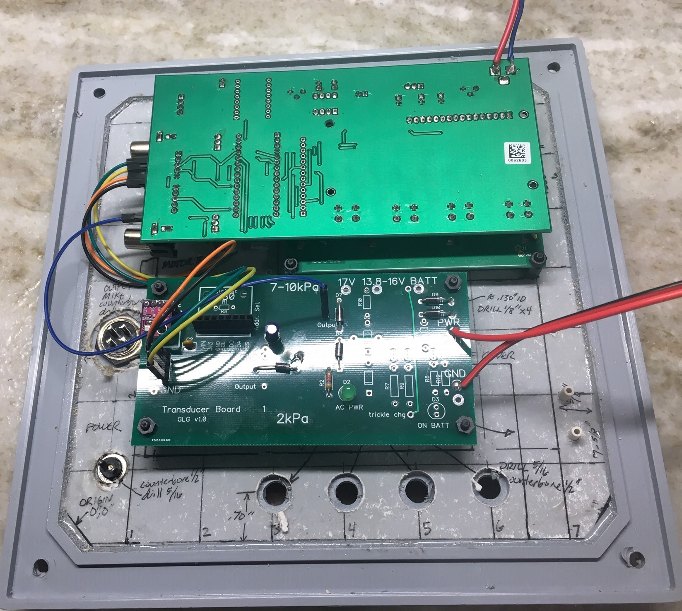
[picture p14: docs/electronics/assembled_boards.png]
    

    a) wire on perfboard and make mechanically stable

    b) Redesign the Transducer/Power supply board to fit this part

    c) Create their own printed circuit board of their own design,

1. Transducer/Power Supply board is mounted on M3 0.60” standoffs at the prescribed location,
taking care so that it will not interfere with the glued battery.
1. The UF Team tasked me on Wednesday April 22 with mounting two plenums for the flow
transducer tubing INSIDE the enclosure. The LifeMech team should skip this on their prototype and
we will provide them exterior to the box. Photo below shows where I placed them. In future builds
we will move the battery off-center so that the plenums can be mounted both on the same side.

    
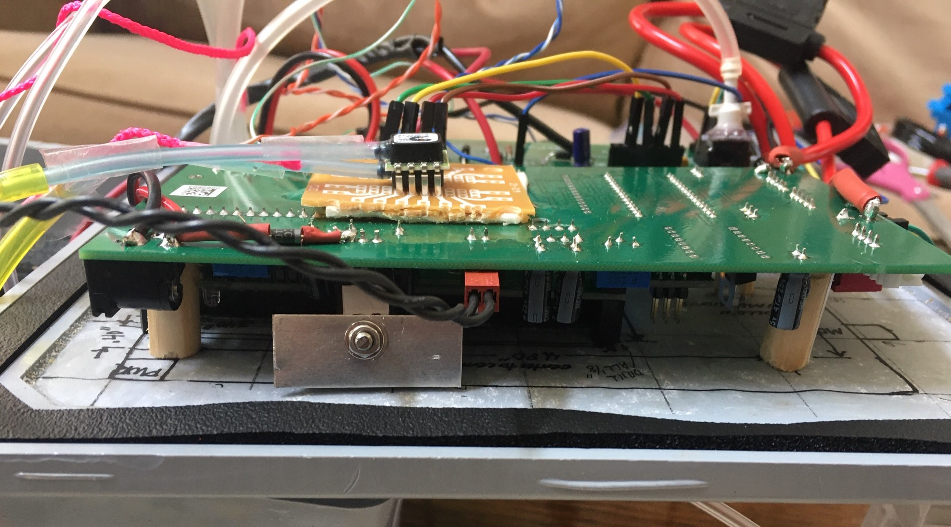
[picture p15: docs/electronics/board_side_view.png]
    

    OPTIONAL home made heatsink on the 5V regulator. Not necessary unless operated in an non-
    airconditioned environment. A small piece of any metal provides additional heat radiating capacity.
    Prevent contact with any other portion of the board as this may be at a voltage potential.

1. Manufacturer may choose to use four push buttons or a 4-switch Normally Open membrane switch
assembly. Mount the chosen pushbuttons and use wiring with very careful soldering to the bring the
four pushbuttons individually in parallel with the onboard connections to the (unnecessary) on board
pushbuttons. #22-#28 stranded wire may be utilized.

1. Output to Solenoids: Mount the output CB MICROPHONE JACK (Part:
https://www.amazon.com/PIN-PANEL-MOUNT-MICROPHONE-CONNECTOR/dp/B00H579TXU )
to the front panel and wire to the ASHHAR BOARD 1.0 as described, either with soldered wires or
with BNC or RCA Phono connectors.

    MOTORA to Pin 1

    MOTOR B to Pin 2

    GROuND to Pin3 and Pin 4

    The final product from commercial manufacturers must have 2 Amp fuse in each solenoid line. In
    this photo you can see that I did the best I could as all I had was #12 gauge fuse assemblies:

    

    NOTE ALSO that I have a (black cable) extension on the USB connector on the Arduino to make it
    easier for me to add and test code. You can REMOVE THIS before clinical delivery.

1. Connector to go to solenoids: 4-pin microphone plug: https://www.amazon.com/4-PIN-CB-
MICROPHONE-PLUG/dp/B00H572J3W Wire with shielded cable with 3 or more stranded
conductors (#16-#22) (example: https://www.homedepot.com/p/Southwire-By-the-Foot-22-4-Gray-
Stranded-CU-CL3R-Shielded-Security-Cable-57572499/204725191 ) with the shield connected to
ground (pins 3 and 4) and pin 1 connected to the INSPIRATORY solenoid and pin 2 connected to the
solenoid driving the EXPIRATORY pneumatically operated valve; the other wire on each solenoid is
connected to ground.

1. Air pressure monitoring: If possible, use 2mm tubing and 2mm brass tubes. If this is not
possible, then: Utilizing standard automobile vacuum tubing fittings such as 1/8” x 1/8” (from:
https://www.amazon.com/Swordfish-61120-Vacuum-Connector-Assortment/dp/B07HV8CVZ8 ) ,
mount and glue-secure barbs through the front panel. Using flexible tubing, connect from the inner
barbs to the

    a) manufactured nipple barb on the BMP (AIRWAY PRESSURE)

    b) upstream and downstream barbs from the ventilator airway components to the barbs on the chosen differential pressure transducer.

    I prefer to have 1/8” barb nipples for connections to small plastic tubing, such as the 1/8” fittings from
    this kit: [https://www.amazon.com/Swordfish-61120-Vacuum-Connector-Assortment/dp/B07HV8CVZ8](https://www.amazon.com/Swordfish-61120-Vacuum-Connector-Assortment/dp/B07HV8CVZ8); but for the BMP280 utilize one of the 1/4” x 1/8” adapters, glue the 1/4” side
    AROUND the bmp280 to the board itself, being careful NOT to get glue inside on the BMP280 chip.

    In the following photos, the tubing from the PATIENT side of the expiratory physical obstruction is
    marked throughout its course with red string:

    

    NOTE: If the flow measurements have the wrong sign, reverse the connections inside the box.

    

21. Provide a 2-3” 16 ohm speaker for the sound output and mount to an internal surface of the box.
22. Be certain that there will be **no mechanical or electrical conflict** when the top is affixed to the
board.

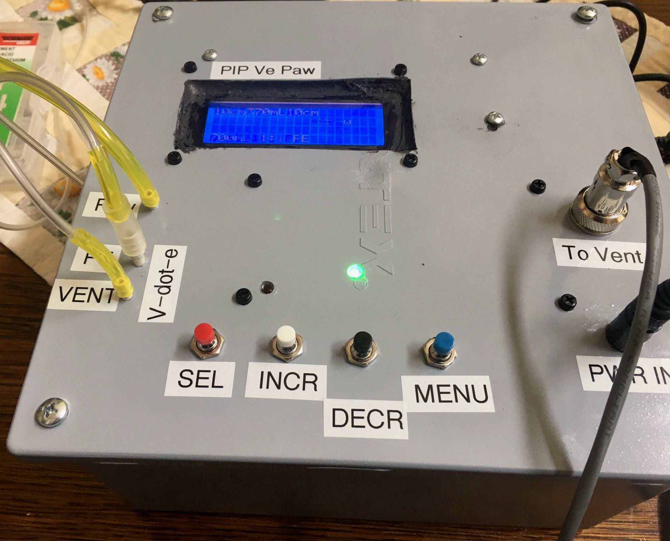
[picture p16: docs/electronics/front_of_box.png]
  

### WIRING UP PERIPHERALS

We have standardized on giving ONLY 3.3VDC to the I2C devices – wire ONLY the 3.3V output from
the board to the V-in terminal of the Transducer board. Depending on what analog transducer you may
be using, you will need to choose what voltage goes to the +5VDC – if you even use U7 or U8. These
are NOT used on the standard FDA submission version from UF

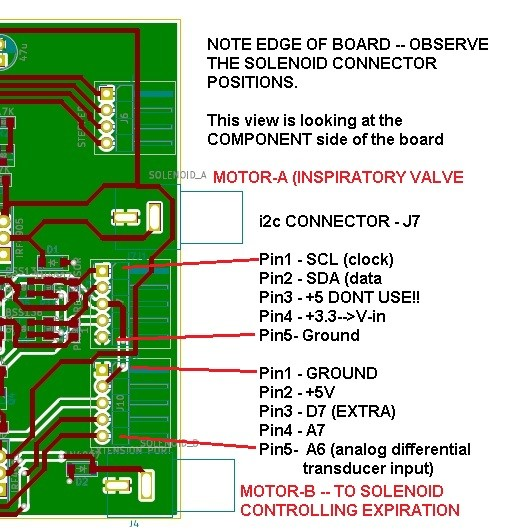
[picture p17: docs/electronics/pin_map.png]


#### WIRING TRANSDUCER BOARD I2C CONNECTIONS

Make the following connections, using either secure pin connectors or soldered wiring:

Main Board J7 Transducer Board Left-Side I2C connector
Pin 1 – SCL (clock)--------------------------SCL
Pin2 – SDA (data)----------------------------SDA
Pin3 DO NOT CONNECT to I2CBus----NO CONNECTION
Pin 4 3.3VDC---------------------------------VIN
Pin5 Ground----------------------------------GND

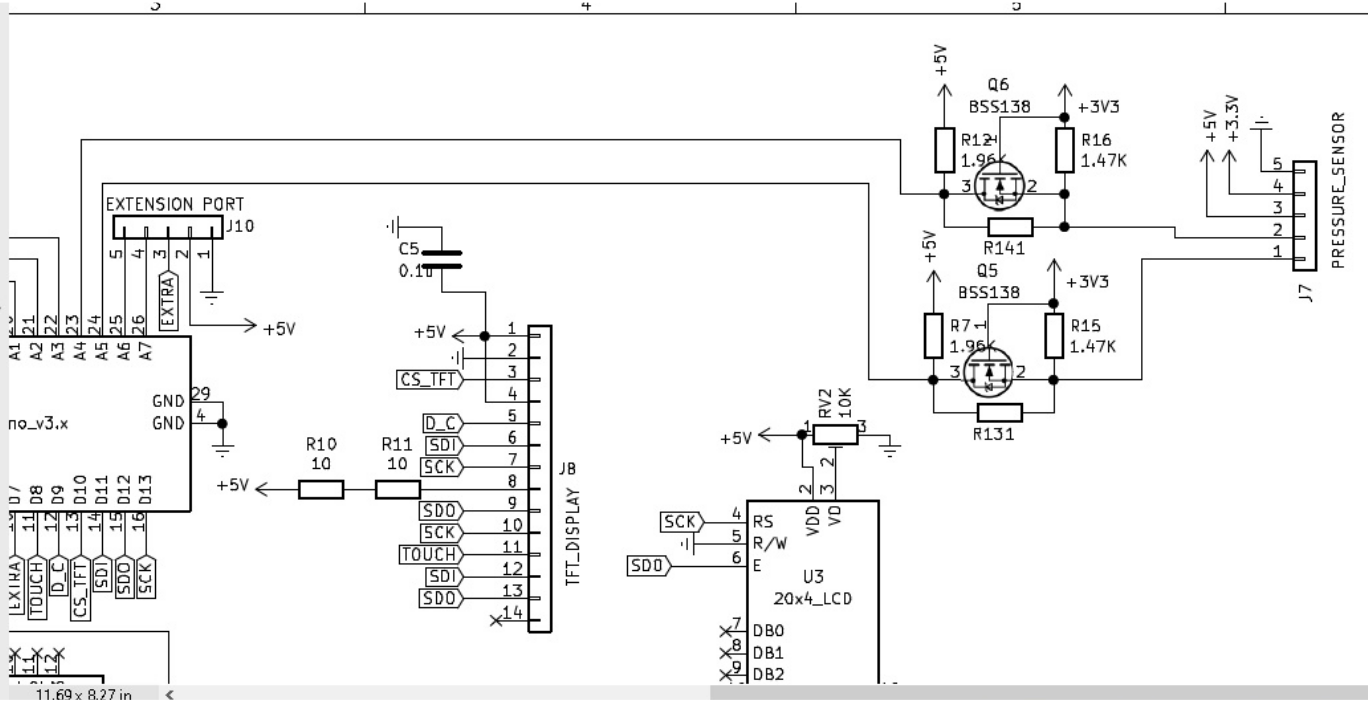
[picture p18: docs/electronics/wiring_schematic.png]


### SOFTWARE SETUP

TODO: Fix this such that pulls from github and installs automatically

Because the code for our project was developed by volunteers literally around the world, most of whom did NOT have access to the same discrete parts, we had to develop with widely varying, but functionally equivalent hardware. As a result it is easiest if you equip your ArduinoIDE as follows:

1. An overview on how to install libraries: [https://www.arduino.cc/en/Guide/Libraries](https://www.arduino.cc/en/Guide/Libraries)
1. Download and install this BMP180 Library: (don’t unzip it);
[https://groups.io/g/VentilatorDevelopers/attachment/1241/0/BMP180MI.zip](https://groups.io/g/VentilatorDevelopers/attachment/1241/0/BMP180MI.zip)

Possible alternates:

[https://bitbucket.org/christandlg/bmp180mi/](https://bitbucket.org/christandlg/bmp180mi/)

A complete set of instructions and another source for that library can be found here (strongly suggest
you read this):

[https://www.ardu-badge.com/BMP180MI/zip](https://www.ardu-badge.com/BMP180MI/zip)

We don’t actually USE this library, but your life will be easier if you just go with the flow here.

1. Download and install the ssense version of the BMP280 library:

[https://create.arduino.cc/projecthub/dragos-iosub/arduino-bme280-sensor-how-to-115560](https://create.arduino.cc/projecthub/dragos-iosub/arduino-bme280-sensor-how-to-115560)

1. SETTINGS that may be of importance to you

|File| Action| Source Code|
|--|--|--|
|Vent.h | Must uncomment the proper one to get the correct code as part of your compile for the flow transducer.|`#define ANALOGDIFFTRANSDUCER // if using the 2kPa analog transdcuer`|
|||`#define I2CDIFFTRANSDUCER // if using the I2C transducer`|
|||
|Vent.h |Get the right display uncommented!!|`#define LCDDISPLAY 2004`|
|||`//extern LiquidCrystal_I2C lcd;`|
|||`//#else`|
|||`//#define LCDDISPLAY 1602`|
|||
|Vent.h |Must uncomment to use the BMP280 (versus BMP180)| `#define USE_BMP280 1 /// set to 0 if not using the BMP280`
|||
|Vent.h |I2C flags of how the bus is working|`#define I2C_BUSY (0x99)`|
|||`#define I2C_READY (0x38)`|
|||
|Vent.h |Where to find the bmp180 library. Trying to root it out of the code is much harder than just loading it...... |`// LIBRARIES`|
|||`// BMP180 https://groups.io/g/VentilatorDevelopers/message/1241`|
|||
|Vent.h |Very important file. You must use the ssense type of BMP280 library.| `#include <sSense-BMx280I2C.h> // Download link halfway down this page:`
|||`//https://create.arduino.cc/projecthub/dragos-iosub/arduino-bme280-sensor-how-to-115560`
|||
|.ino file| Each gives terse explanation. Remember that debug code will take away crucial RAM space and may cause instabilities of the running code so only using temporarily.| `//#define DEBUG // Turn on to debug`|
|||`//#define SHOWINSTANTFLOW // to see calculations of instantaneous flow`
|||`//#define TOTALTIDAL-DISPLAY // to see the tidal volume calculated each breath`
|||`//#define BMP280DEBUG // to see serial port related to BMP`
|||`//#define AIRWAYPRESSURECHECKING // help me figure out why the valve isn't opening`
|||`//#define SERIALPRINT; // gives a load ofprintouts on pressure monitoring`
|||`//#define SMOOTHPRESSURERUN //Investigating expiratory ringing and assist control ventilation`
|||`//#define DIGITALPRESSURESPY // to see measurements related to digital I2C diff press`
||||
|.ino file| Different BMP280’ breakout boards may express different addresses.....beware!| `#define BMP_ADDRESS 0x76 // *****GLG FOR THE KEE-YEE!!!!`|
||||
|.ino file| The uBitx transceiver uses different wiring to the LCD display – be certain that you have the right pins selected if you change hardware. |`//static LiquidCrystal lcd(8, 9, 10, 11,12, 13); //when using ubitx board`|
|||`LiquidCrystal lcd(13,12,11,10,9,8); //when using the GAINESVILLE VENTILATOR`|
|Vent.h| Pin assignments for your hardware MUST be correct or things won’t go as planned.|`#define ALARM_PIN 6`|
|||`#define FN A0`
|||`#define UP A1`
|||`#define DOWN A2`
|||`#define ON_OFF A3`
|||`#define TFT_CS 10`
|||`#define TFT_RS 9`
|||`#define CS_PIN 8`
|||`#define MOTOR_A 2`
|||`#define MOTOR_B 3`
|||
||Defines the number of slices in time the respiratory cycle is set to. I don’t recommend increasing this.|`#define MAX_PHASES 20 //At 40 the machne could barely keep up`

INITIAL Qualification:

1. Apply battery power (if selected) and verify that the RED battery light comes on and the LCD
powers up.
1. Apply power from the 15V medical grade power supply and verify that the GREEN AC power
led comes on.
1. Further function testing will be provided shortly.

APPENDIX Ashhar 1.0 Board

Schematic:

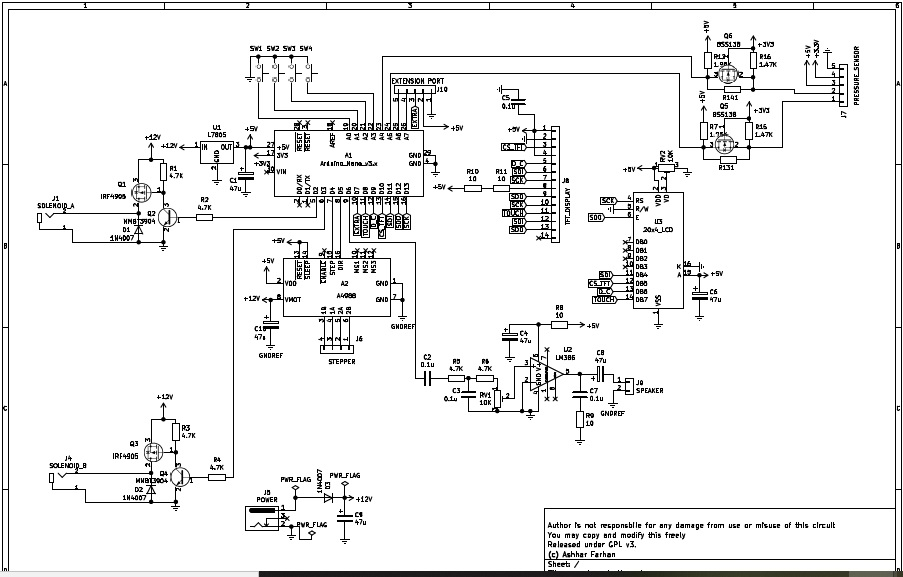
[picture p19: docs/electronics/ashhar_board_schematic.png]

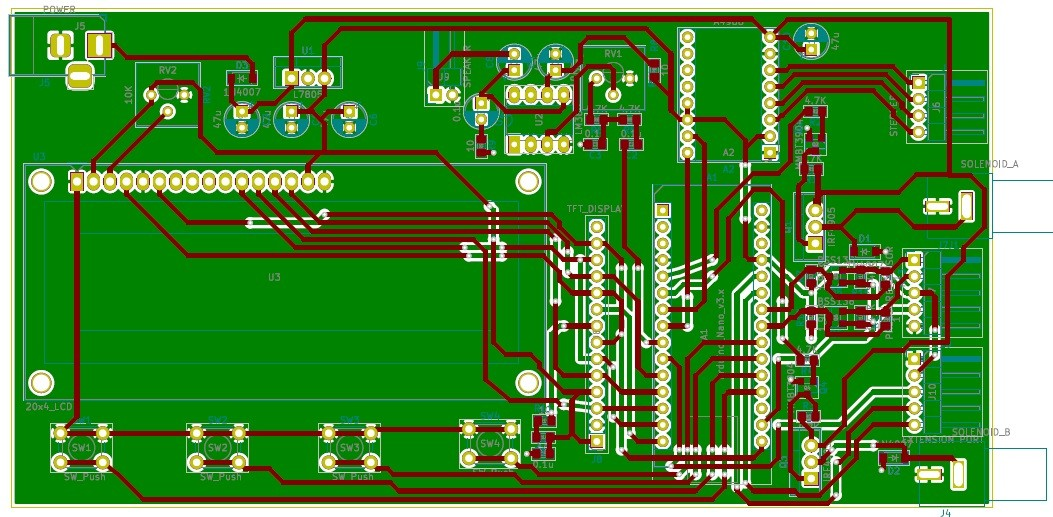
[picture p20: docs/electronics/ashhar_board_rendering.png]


APPENDIX: Schematic for Transducer Board and Parts Values

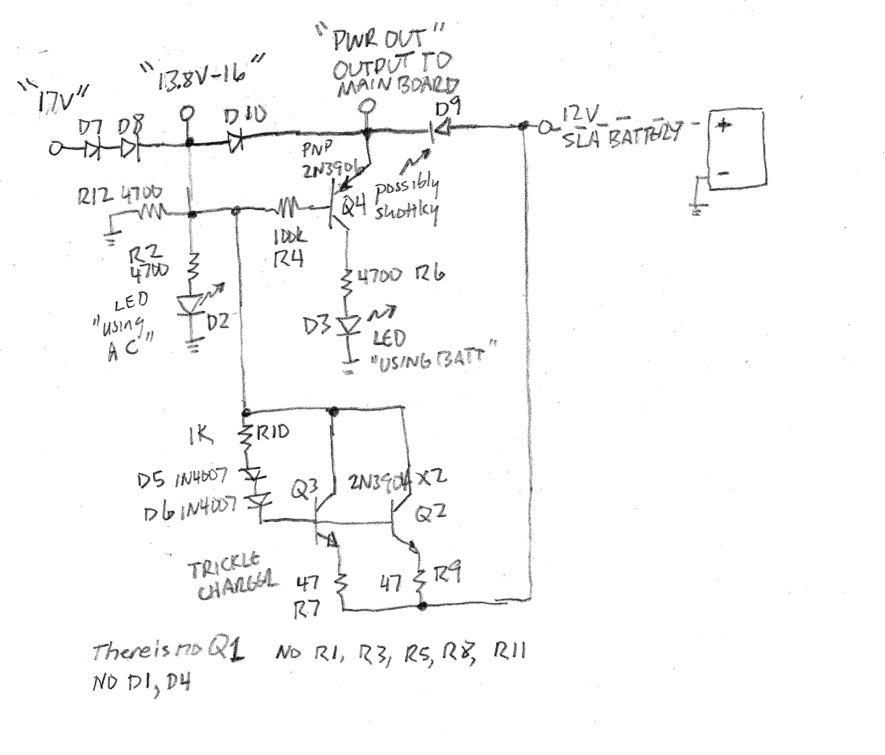
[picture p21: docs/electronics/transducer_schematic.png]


Schematic of “Transducer” Board which includes a Diode-OR connection for two different DC sources,
and a small trickle charger (constant current) for a 12 volt sealed lead acid battery.

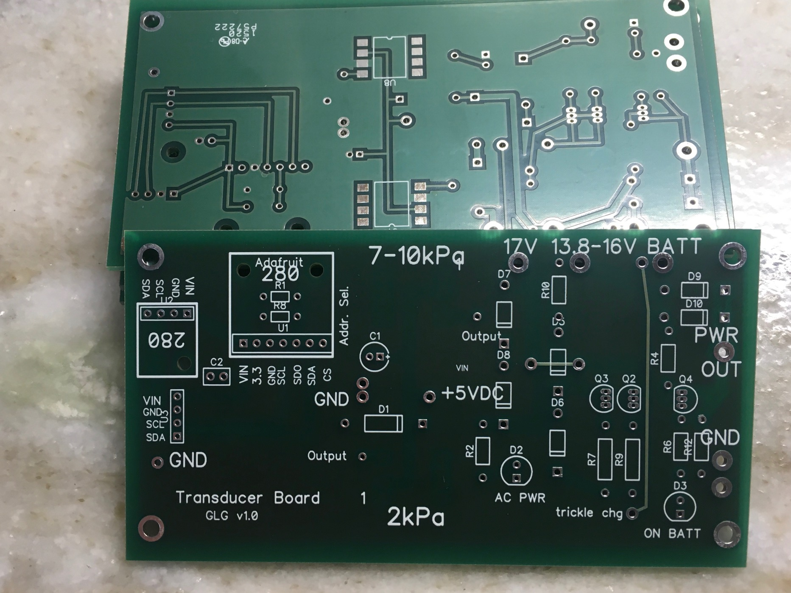
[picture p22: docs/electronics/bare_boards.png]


||Part|Details | Comments|
|--|--|--|--|
||Adafruit 280| Breakout board for Adafruit BMP or BME 280 (either works) R1 and R8 are NOT needed; they are there to change the address from 0x77 if desired.| Although this board is capable of operating at 5V bus voltage, we intentionally operate the bus at 3.3V because many differential pressure transducers require 3.3 V bus and will be damaged by 5V|
||Additonal “280”| This was laid out to fit a certain clone (“Kee-Yee”) of the bmp280 board – optional alternative – not needed and may be used to provide connections to the I2C differential pressure transducer.| There are many different BMP280 breakout boards on the market and they all appear to use **DIFFERENT PINOUTS.** Observe signal names carefully.
||C1| Electrolytic 20-47uf @ >20VDC||
||C2| 0.1V @ >20VDC|
||Input I2C connector| Solder or use 0.1” header as desired|
||ALL RECTIFIER DIODES (D7, D8, D6,D5, D9, D10)| 1N4007 1Amp or equivalent||
||D2 “AC PWR”| Green LED (manufacturer choice of size)|
||D3 “ON BATT”| Red LED (manufacturer choice of size)|
||Q1| none||
||Q2 Q3| 2N3904 NPN transistors||
||Q4| 2N3906 PNP transistor||
|||
||R1| none||
||R2| 4700 ohm 1//4 watt||
||R3| none||
||R4|100K ¼ or 1/8 W|
||R5| none||
||R6| 4700 ohm 1/4W|
||R7| 47 ohm ½ watt||
||R8| none|
||R9| 47 ohm ½ watt||
||R10| 1000 ohm ¼ watt||
||R11| none||
||R12| 4700 ohm 1/4W||

APPENDIX: Suggested Important FMEA topics

Assumptions: Single failures
Other input values normal.

|Function|Faliure|Cause|How weworked to show it.|
|--|--|--|--|
|Move medical gases in and out of the patient in the right amount, the right pressure, and the right timing.| Wrong gas.| Hospital line failure We can’t. |External to our device|
||Wrong mix %| Blender failure| Require external oxygen monitor.|
||Too much inspiration.| Regulator failure| Auto release of pressure if limit exceeded, auto opening of expiratory valve. High volume alarm. |
|| Too much inspiration| Patient compliance improves| High Vol alarm signals to clinician
|| Too much inspiration| Pressure sampling line gets plugged meaning we can no longer measure pressures| Alarm, either low or high pressure, and alarms, high flow.|
||Too much inspiration| Software hang| Watchdog timer will release software and reset and pause and rezero.|
||Too much inspiration| Timing failure| Extraordinarily unlikely if device passes initial quality testing. There are NO blocking calls in the software.|
|| Too little inspiration| Mechanical regulator failure| Low Vol and Low flow alarms.|
||Too little inspiration| Breathing circuit disconnection| Low Vol and Low flow alarms.|
||Too little inspiration| Plugged ETT| High pressure alarm and low volume alarm will sound.|
||Too little inspiration| Faulty flow measurement| Clinician observation of the patient as a confirmation of unusual reported values. Also blood gases.|
||Too little inspiration| Software failure “hang”| Extremely unlikelyl after long term testing of software; requires non-repeatability of code or memory leak, which would be unlikely not to show witihn a thousand cycles.|
||||Watchdog timer will reset the entire processor.|
||Too little inspiration| I2C bus failure| We designed a complete sysetm to deal properly with this extremely rare pheomenon and to continue to ventilate in an open loop manner as previously programmed.|
||Too high a pressure| Patient or ETT condition| Automatic release of pressure by both closing inspiratory valve and opening expiratory valve. High Pressure alarm.
||Too high a pressure| Clinician mis-setting| Automatic release of pressure above set limit and High pressure alarm|
||Too low a pressure| Disconnection |Low Pressure and low flow alarms.|
||Too low a pressure| Misconnection with gas flow diverted through a leak| While an obstructed leak (into bedclothes) might fool the low pressure alarm, because we measure flow in the EXPIRATORy limb, the low volume will be detected.|
||Too LONG inspiratory effort| Clinician missetting| Limits on I:e and respiratory rate make this very unlikely
||To Short inspiratory effort | Clinician missetting| Limits on I:E and respiratory rate make this very unlikely|
||Failure of ventilation system | Improper voltage from mains, resulting in damaged power supply and failure | Medical grade power supply is function from well below normal mains to well above european mains votages. Battery backup will pick up the supply and indicate the failure with a red LED. Failure of pressure monitiring or flow monitoring system.|
||Faliure of pressure monitoring or flow monitoring system | Failure of I2C buss| Solder connections; operate system at 3.3VDC; carefully developed watchdog system will kick in and provide open loop ventilation of the patient.|
||||
|Physically connect to the patient breathing circuit| Improperly fitting airway connectors. || We use industry standard sizes, so very unikely. Having pre-use checkout by clnical users should detect it

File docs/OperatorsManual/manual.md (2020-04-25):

---
layout: default
title: Operator's Manual
---

PanVent User Manual

| **Version** | **Date** | **Who** | **Comments** |
| --- | --- | --- | --- |
| **1.0** | **4/22** | **sl** | **First\_Draft – using pNeuton existing ventilator manual as template** |
| **1.1** | **4/23** | **sl** | **Continued edits** |
| **1.2** | **4/24** | **sl** | **Updated graphic for rear panel** |

PanVent TM is a Registered Trade mark of the University of Florida Research Foundation

# PanVent

**Pandemic Ventilator**

**Model**  **A**

# Operators Manual



97011

CD-A-005Rev I

_Released 24 April 2020_

Copyright©2020byUniversity of Florida Research Foundation

Manufactured by:

Airon®Corporation

751NorthDrive

Unit6

Melbourne,Florida32934 USA

Tel: 888-448-1238(tollfreeUSA&Canada

+1-321-821-9433

Fax:+1-321-821-9443

**Table of Contents**

[Section 1: General Description 1-1](#section-1:-general-description)

[Section2: Warnings, Cautions, Notes 2-1](#section-2:-warnings,-cautions,-notes)
  * [Warnings 2-1](#warnings)
  * [Cautions 2-3](#cautions)
  * [Notes 2-4](#notes)
  * [Indications for Use 2-6](#indications-for-use)
  * [Contraindications 2-6](#contrainditions)
  * [Medical Symbol Key 2-7](#medical-sybol-key)

[Section 3: Controls and Patient Safety Systems](#section3:-controls-and-patient-safety-systems)
  * [Front Panel 3-1](#front-panel)
  * [Rear Panel 3-3](#rear-panel)
  * [Unique Device Identifier 3-5](#unique-device-identifier)
  * [Internal Patient Safety Systems 3-6](#internal-patient-saftey-system)

[Section 4: Operating Instructions 4-1]($section-4:-operating-instructions)
  * [Ventilator Set-up 4-1](#ventilator-set-up)
  * [Operational Verification 4-2](#operationl-verification)
  * [Patient Ventilation 4-3](#patient-validation)
  * [Interrelationship of Volume and Rate Controls 4-4](#interrelationship-between-volume-and-rate-controls)
  * [Oxygen Control 4-5](#oxygen-control)
  * [Hypobaric Operation 4-5](#hypobaric-operation)
  * [Disconnect Alarm 4-5](#disconnect-alarm)

[Section 5: Patient Circuit 5-1](#section-5:-patient-circuit)
  * [Adult/Pediatric Circuit 5-1](#adult/pediatric-circuit)
  * [Ventilator Connection 5-2](#ventilator-connection)
  * [Single-Use only Devices/Accessories 5-3](#single-use-only-devices/accessories)

[Section 6: Accessories 6-1](#section-6:-accessories)

[Section 7: Theory of Operation 7-1](section-7:-theory-of-operation)
  * [Pneumatic System Diagram 7-1](#pneumatic-system-diagram)
  * [Pneumatic System Description 7-2](#pneumatic-system-description)
  * [Tidal Volume and Rate Control System 7-3](#tidal-volume-and-and-rate-control-system)
  * [Mandatory Breath Pressure Control System 7-5](#mandatory-breath-pressure-control-system)
  * [CPAP Demand Flow Breathing System 7-5]()
  * [Assist-Control System 7-5]()
  * [Oxygen Delivery System 7-6]()
  * [MRI Compatibility 7-9]()
  * [Disconnect Alarm 7-10]()
  * [Low Gas Supply Alarm 7-11]()

[Section 8: Troubleshooting 8-1]()

[Section9.CleaningandMaintenance 9-1]()
  * [Cleaning the Ventilator 9-1]()
  * [Cleaning/Disinfecting the Patient Circuit 9-1]()
  * [Routine Maintenance 9-1]()
  * Factory Preventive Maintenance 9-1]()

[Section 10: Specifications 10-1]()
  * [General Description 10-1]()
  * [Ventilator System Performance 10-1]()
  * [Alarm System 10-2]()
  * [Environmental and Physical Characteristics 10-3]()
  * [Power Sources 10-3]()

[Section 11: Limited Warranty 11-1]()
[Section 12: Index 12-1]()

## Section 1: General Description

PanVent TM (pronounced Pan Vent) is a small,light weight pandemic ventilator designed for
use on adult patients from pediatric to adult in size, 23 kg or greater. It is a time cycled,
 flow limited ventilator providing Intermittent Mandatory Ventilation(IMV). In this mode of
 ventilation, an adjustable respiratory rate and tidal volume are delivered to the patient.
 The patient is allowed to breathe spontaneously between the mandatory breaths with minimal
  work of breathing. A built-in PEEP/CPAPsystem can be set to provide expiratory positive
   pressure. The delivered oxygen gas composition is supplied by a gas source external to
 the ventilator and is adjustable to 65% or 100%, with oxygen as the driving source gas.
  The ventilator can accept and deliver oxygen compositions varying from 21% to 100%.

PanVent TM is an electronically controlled pneumatic ventilator. Electrical
power is not required for patient ventilation. PanVent TM has been specifically designed
for patient support during pandemic and non-critical care unit mechanical ventilation.
 It maybe used during intra and inter-hospital pandemic, in aircraft, on ambulances,
 in emergency rooms, MRI and other radiologysuites.in regular hospital settings as well
 as converted medical facilities such as convention centers and indoor stadiums.

## Section 2: Warnings, Cautions, Notes

The PanVent TM Ventilator is intended for use by properly trained personnel
under the direct supervision of licensed medical Physician or Practitioner only.
Personnel must be come thoroughly familiar with this Operators Manual prior to
using the PanVent TM Ventilator on a patient.

As used in this manual, the following terms mean:

**Warning:** Indicates the possibility for injury to the patient or the operator

**Caution:** Indicates the possibility of damage to the device

**Note:** Places emphasis on an operating characteristic

### Warnings

This manual serves as a reference. The instructions in this manual are not
intended to supersede the physician's instructions regarding the use of the
PanVent TM Ventilator.

The operator should read and understand this entire manual before using the
PanVent TM Ventilator.

**DO NOT** use the PanVent TM Ventilator in conjunction with
anesthetics or in contaminated(hazardous, explosive) atmospheres. Only compressed oxygen may be used.

**DO NOT** use conductive(anti-static)patient breathing circuits. The
*only* approved patient circuits for use with PanVent TM Ventilator are the circuits listed in Section5
of this manual. Any other patient circuit should **NOT** be used and may lead to patient harm.

The Operational Verification tests as described in this
manual(Section4) must
be performed prior to connecting a patient to the ventilator. If the ventilator
fails any of the tests it must be removed from pandemic clinical use.
**DO** **NOT** return the unit to pandemic clinical use until all repairs has
been completed by an Airon approved repair facility and all operational
verification tests are acceptable.

The PanVent TM Ventilator has been designed for use on adult and pediatric patients.
The PanVent TM cannot deliver operator adjusted tidal volumes less than 2360ml.
**DO NOT use the PanVent TM Ventilator on neonatal or infant patients, or small children.**

To protect the patient from high air way pressures, insure that the Peak Pressure
 control is adjusted appropriately.

### Cautions

**DO** **NOT** attempt to service the unit. Service may only be performed
by Airon Corporation authorized engineers. The Preventative Maintenance program
requires a general service and calibration every two years. Only original
manufacturer parts and accessories should be used.

Any attempts to modify the hardware of this device without the express written
approval of Airon Corporation University of Florida Research Foundation (UFRF)
will void all warranties and liabilities.

Do not immerse the PanVent TM Ventilator or allow any liquid to enter the controller
case or the inlet filter. Clean as directed in Section 9, Cleaning and Maintenance.

### Notes

In the USA the PanVent TM Ventilator is a restricted medical device intended for
use by qualified medical personnel under the direction of a physician.

**Additional Warnings, Cautions, and Notes are located throughout this manual.**

### Indications for Use

The PanVent TM Ventilator is intended for continuous mechanical ventilation
of patients in the following patient populations and use locations:

Patient population-adult COVID-19 / pediatric patients **23 Kg** or greater
who require the following general types of ventilatory support:
* positive pressure ventilation delivered invasively(via an ET tube) or
non-invasively(via a mask)
* CMV and assist-control IMV modes of ventilation
* with or without PEEP
* with oxygen or a mixture of air and oxygen

The ventilator is suitable for use in:
* Pre-hospital pandemic applications including accident scene, emergency rescue vehicles
* Hospital ICU pandemic applications including emergency, radiology, surgery,
post- anesthesia/recovery and MRI departments
* Air pandemic via helicopter or fixed wing

### Contraindications

The following conditions contraindicate the use of the

PanVent TM Ventilator:

* Patients under going procedures with flammable anesthetic gasses.
* Patients under going hyperbaric treatment.
* Infants and neonatal patients requiring tidal volumes less than 360ml.

#### PanVent TM Airon's Medical Symbol Key (Stopped reviewing and editing here – Sem 4/22/20)

|Symbol| Meaning|
|---|---|
||Consult Instructions of Use|
||CE Marked|
|  |Authorized Representative in European Community |
| | Model(Part)Number |
| | Lot Number |
| | Do Not Reuse |
| | MRI Conditional (3T) |
| | Manufactured Date |
| | Manufacturer |
| | Use By Date |
| | Keep Dry |
| | Caution, serious injury or device damage may occur by disregarding the instructions accompanying this warning symbol. |

## Section 3: Controls and Patient Safety Systems
### Front Panel
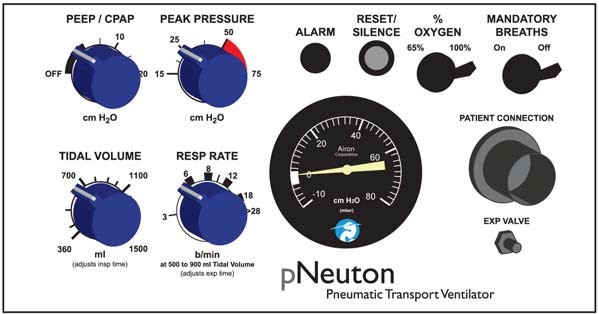
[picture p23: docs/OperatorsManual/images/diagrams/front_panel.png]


| Interface | Function |
| --- | --- |
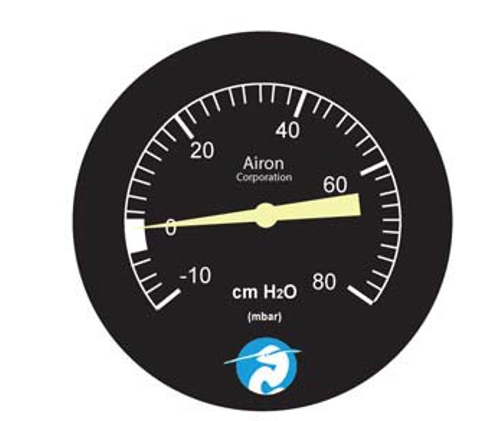
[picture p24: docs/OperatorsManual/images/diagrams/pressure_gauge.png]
| | Pressure gauge, patient circuit pressure|
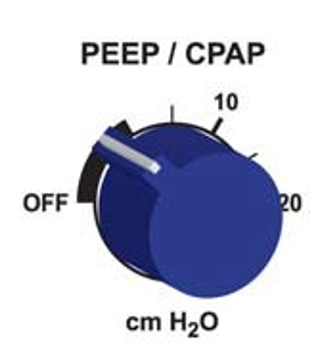
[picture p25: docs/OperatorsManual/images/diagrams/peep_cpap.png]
| | PEEP/CPAP control: calibrated, range 0 to 20 cm H2O|
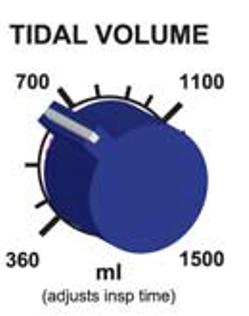
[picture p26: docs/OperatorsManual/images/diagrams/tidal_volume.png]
|| Tidal Volume control: calibrated, range 250 to 600 ml |
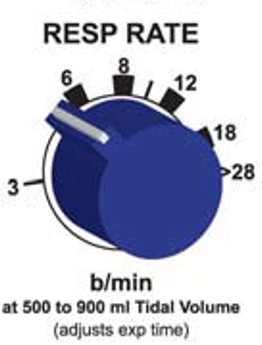
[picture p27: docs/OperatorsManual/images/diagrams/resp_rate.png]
| | Respiratory Rate control: calibrated, range 103 to 30 bpm dependent on tidal|
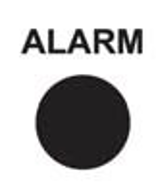
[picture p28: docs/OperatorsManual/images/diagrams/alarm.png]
| | Alarm visual indicator |
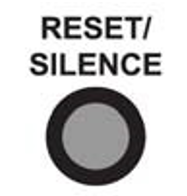
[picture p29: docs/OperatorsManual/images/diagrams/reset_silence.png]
|  | AlarmReset/Silence,1 minute |
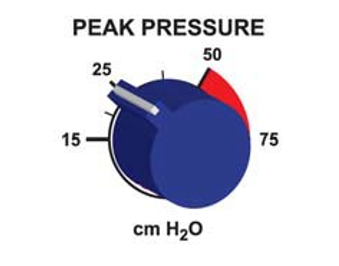
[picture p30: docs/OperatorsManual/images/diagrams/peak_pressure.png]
|  | Peak Pressure control of mandatory breaths: calibrated, range 15 to 40 cmH2O|
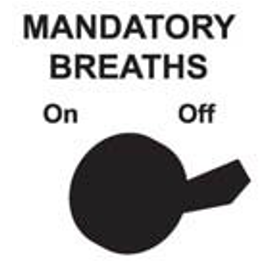
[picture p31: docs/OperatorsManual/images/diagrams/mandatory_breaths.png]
| | Mandatory Breath control, turns on or off mandatory breath system |
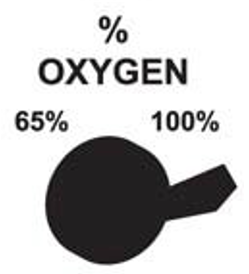
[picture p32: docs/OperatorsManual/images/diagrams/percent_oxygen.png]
|  | Oxygen control, select either100% or 65% |
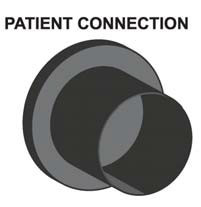
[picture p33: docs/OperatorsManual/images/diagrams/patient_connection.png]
| | Patient Circuit connection, see Section 5 for a complete description of the patient circuit and it's attachment to the front panel|
| | Expiratory Valve connection |

### RearPanel

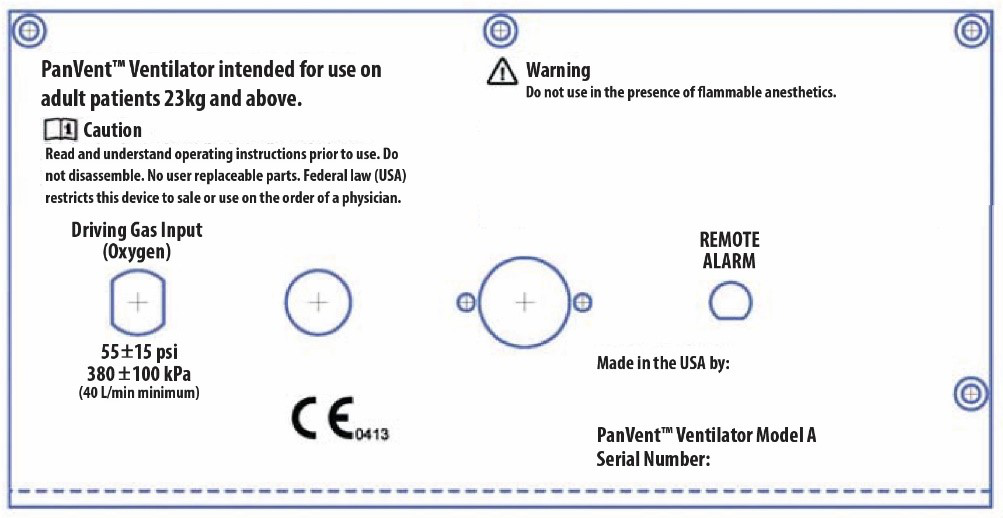
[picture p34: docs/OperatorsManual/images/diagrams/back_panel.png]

 Driving Gas Input(oxygen), DISS connection, requires 55+15psi(380+100kPa),(**40liter/minute minimum**)

| Interface | Function |
| --- | --- |
|**TODO: image here** | Alarm, Low Driving Gas|
| **TODO: image here** | Ambient Air Inlet Filter |
| **TODO: image here** | Remote Alarm out put |

### Unique Device Identification (UDI)

Pursuant to the U.S.FDA Unique Device Identification (UDI) Rule, each device must
bear a UDI code. The UDI for PanVent TM ventilator is located under the. "Serial Number:" labeling, in plaintext, on the back panel of the device. The UDI code consists of one Device
Identifier (DI) and potentially four Production Identifiers (PI).

Therefore, UDI=DI+PI. Production identifiers are required if the information appears on the product(box) label. The UDI on the product(box) label appears in both plaintext and
machine-readable format. The numbers in the parentheses indicate different parts
of the UDI, as applicable to the device:

(01) Device Identifier

(10) Batch/LotNumber

(11) Manufacturing/Production Date

(17)Expiration Date

(21)Serial Number

The format for Manufacturing/Production date and Expiration date within the UDI
code is: YYMMDD

* YY=tens and units of the year(e.g.2014=14)
* MM=number of the month(e.g. January=01)
* DD=number of the day(e.g. third day=03)
* e.g. January03,2014=140103

An example UDI for the PanVent TM ventilator is as follows:

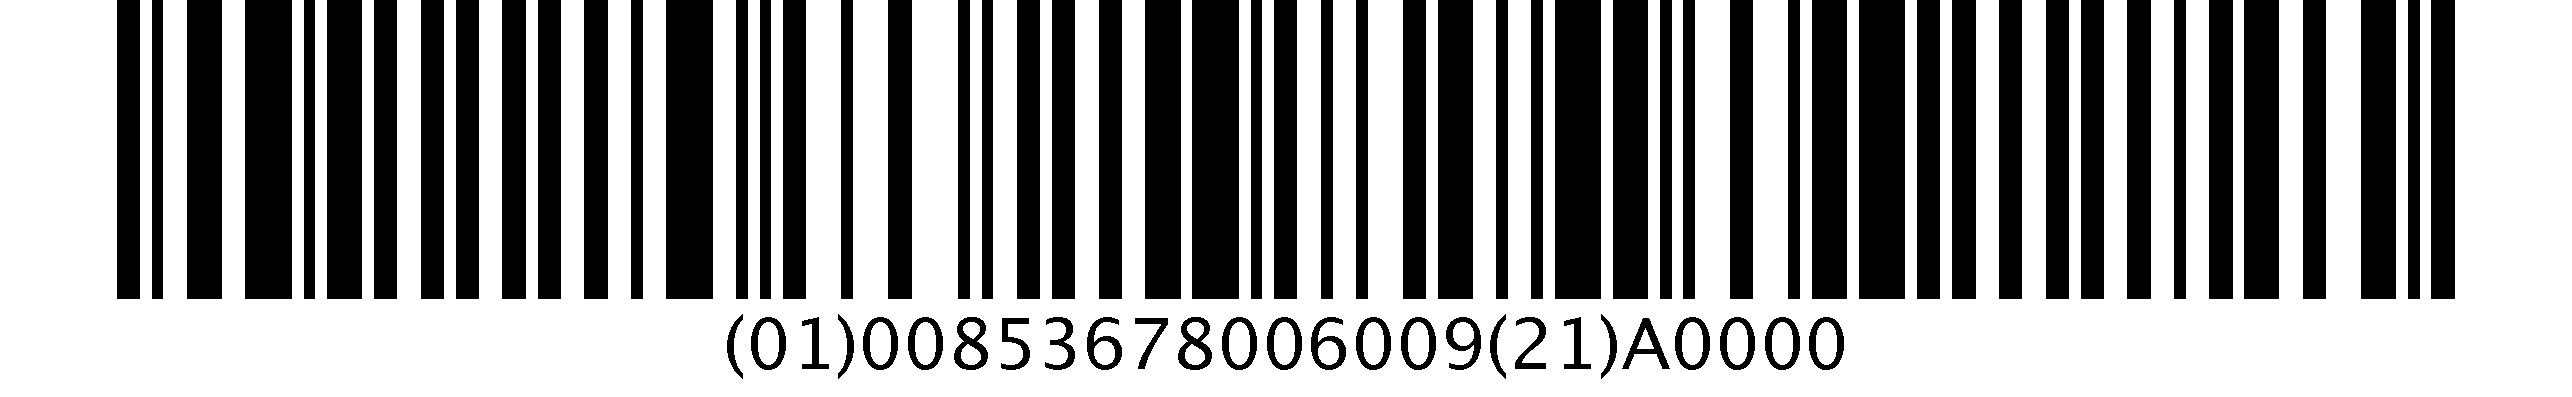
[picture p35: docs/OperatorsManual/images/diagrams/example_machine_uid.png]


Device Identifier=00853678006009

Serial Number=A0000

The Device Identifier portion of the code may be entered into Access GUDID to
obtain information about the product.[http://accessgudid.nlm.nih.gov/](http://accessgudid.nlm.nih.gov/)

### Internal Patient SafetySystems

The ventilator has several internal safety systems. These systems insure patient safety in the event of ventilator malfunction.

#### High Pressure Release

The patient circuit peak pressure is adjustable using the Peak Inspiratory Pressure
control. This control can be set from 15 to 60 cmH2O. The factory preset value is 40
cmH2O. In addition to this software control, there is an internal safety pressure release valve. This
valve will automatically limit circuit pressure to approximately 3 cmH2O, regardless of the setting of
the Peak Inspiratory Pressure control.

#### Anti-Suffocation System

An internal safety system will allow the patient to breathe on his or her own in the event of  
ventilator malfunction. At approximately 32 cmH2O negative pressure an internal valve will open
allowing unimpeded ambient air to enter the patient circuit for the patient. This system is always
available to the patient, irrespective of control settings, including PEEP/CPAP.
 **Software implementation too? Gordon?**

#### Low Gas Supply Pressure Alarm – Dave/Gordon: confirm we do not have this

When ever the driving gas supply pressure drops below the safe operating pressure the visual alarm
indicator will illuminate and an internal pneumatic audible alarm will sound. This low pressure alarm
will occur when the source gas pressure drops below 30psi(200kPa).The alarm will continue to sound
until all pressure has been lost in the system or when pressure is re-established
to at least 35psi (250kPa).

 **WARNING:** The Low Gas Supply Alarm will only activate for a very
short period of time if the gas supply abruptly ceases as can happen if the supply
gas becomes disconnected. Always insure that the supply gas is secure and
operating at the proper pressure.**??**

#### Disconnect Alarm

The ventilator automatically monitors patient pressure at all times. If there is a disconnection in the
patient circuit the visual alarm indicator will illuminate and the audible alarm will sound. The alarm
activates when either of the following conditions occur:

|Mandatory Breaths Status| Alarm Behavior|
|--|--|
|ON| if a circuit pressure of at least 15 cmH2O is not sensed within 22 seconds after the last breath – Gordon, confirm or modify|
|OFF | if the circuit pressure is less than 5 cmH2O for  22 seconds. Gordon, confirm or modify|

**The Disconnect alarm may be silenced for 1 minute by pressing the alarm Reset/Silence button.**

**NOTE:** Always use an external oxygen monitor to insure the desired oxygen percentage is delivered to
the patient.

## Section 4: Operating Instructions Ventilator Set-up

The following equipment is needed:

1. PanVent TM Ventilator with breathing circuit(see Section 5 for a list of compatible circuits.)
1. Test lung, (1 or 3 Liter bagrigidwall,AironPart#21002 suggested)
1. Spirometer
1. Watch

When ready:

1. Attach breathing circuit to ventilator as described in Section5.
1. Attach the test lung to the patient side of the breathing circuit.
1. Set the controls as follows:
  1. **Mandatory Breath** control to On
  1. **% Oxygen** to 21%
  1. **PEEP / CPAP** to Off
  1. **Peak** Pressure to 40 cmH2O
  1. **Tidal** volume to 400 ml
  1. **Respiratory Rate** to 12 bpm
1. Attach Oxygen Input on rear panel of the ventilator to a high pressure
oxygen source and turn on the oxygen.

**NOTE:** The ventilator will begin operation at the above settings when the oxygen is turned on. The
alarm will sound. You may press the "Reset/Silence" button to silence the alarm or wait for the unit to
begin ventilating.

### Operational Verification

| VerificationStep | AcceptableRange | Result |
| --- | --- | --- |
| Attach a spirometer to the expiratory valve using the elbow included in the circuit packaging outlet port. After 3 breaths measure the delivered tidal volume. | 4700±470ml | Pass/Fail |
| Count the respiratory rate with a stopwatch. Measure the number of breaths in one minute. | 12±2 breaths per minute | Pass/Fail |
|Remove the test lung and occlude the patient connection on the circuit. Read the circuit pressure from the pressure gauge electronic display on the front of the ventilator. | 450 ±5 cmH2O | Pass/Fail |
|Remove the occlusion and allow the breathing circuit to remain open. Using astop watch, measure the time until the alarm sounds | 22±3seconds | Pass/Fail |
| With breathing circuit remaining open, check that airway pressure reads 0 cm H2O | 0 ±1 cmH2O | Pass/Fail |
| With breathing circuit remaining open, check that flowmeter reads 0 L/min | 0 ±1 L/min | Pass/Fail |

If the ventilator has passed all the above steps it is ready
to return to clinical use. If the ventilator fails to pass any of the following tests do not apply it
to patients. Call your local distributor or Airon Corporation Customer Support at 888-448-
1238(toll free USA & Canada)or+1-321-821- 9433. Discard the unit. **Do not attempt to service the unit.**

 **CAUTION:** Do not disassemble the PanVent TM Ventilator. No
internal user replaceable parts. All service must be performed by Airon Corporation or an approved
service technician.

**Opening the device will negate the warranty. User will be responsible for all repair costs to service the unit.**

### Patient Ventilation

The ventilator operates with the following modes:

* CMV-Continuous Mechanical Ventilation
* Assist Control

Using the Continuous Mechanical Ventilation (CMV) mode, the ventilator provides an adjustable number of
breaths per minute. The tidal volume of these breaths is also adjustable. The patient may breathe
spontaneously between ventilator breaths as desired.

1.	Set the % Oxygen control to the desired FIO2 on the external blender or gas supply
1.	Set the PanVent On switch to On.
1.	Set the Tidal Volume control to the appropriate level by adjusting the pressure regulator – continue manual adjustment until the ensuing exhaled tidal volume displayed in ml on the user interface is within 10% of desired tidal volume
1.	Adjust the Respiratory Rate control to achieve the desired mandatory breath frequency.
1.	Adjust the Peak Inspiratory Pressure control to the desired level by turning the control while occluding the patient circuit and observing the level of pressure generated during a mandatory breath.
1.	Attach the patient circuit to the patient and observe for appropriate ventilation. Adjust as required. External measurement devices should be used to verify ventilation parameters.
1.	Adjust the PEEP control to the desired level.
1.	Adjust for spontaneous breath trigger sensitivity for assist control by the ventilator.
1.	Observe and monitor the patient and the ventilator per your institution's standards. If using a portable gas supply, monitor the supply level to insure there is sufficient gas for ventilation.

### Interrelationship of Volume and Rate Controls

There is an interrelationship between the Tidal Volume control and the Respiratory Rate control which
must be considered while operating this ventilator. The Tidal Volume control is a calibrated control
and will not vary from its setting during normal operation. It will not change if the Respiratory Rate
control is changed. The Respiratory Rate control is calibrated and will not vary
the patient's mandatory breath rate unless changed. However, if the Tidal Volume control setting is
changed the actual respiratory rate may change even if the Respiratory Rate control is not moved.

The ventilator operational characteristics define the reason the rate changes when the tidal volume is
changed. See Section 7 for a detailed description of the ventilator's Theory of Operation.

The Respiratory Rate control is calibrated for tidal volumes between 500 to 900ml. This allows the rate control to be preset with initial set-up of the ventilator on a patient.

Always count the patient's mandatory breath rate when first setting up the ventilator and after any
changes to the tidal volume to assure the patient is receiving the proper respiratory rate.

The mandatory breath inspiratory flow is fixed at 36L/min. Due to this preset flowrate, it is possible
that desired combinations of high tidal volume and respiratory rates may not be available. In
other words, combinations of high tidal volumes and high mandatory breath rates are limited by the
fixed mandatory breath flowrate. If a high respiratory rate is required, a lower tidal
volume may be necessary. Likewise, if a hightidal volume is required, a lower respiratory rate may be needed.

### Oxygen Control
The PanVent ventilator uses the gas mixture delivered to its gas inlet port. See Section 7 for a complete description of these systems. It is recommended that an external oxygen analyzer always be used to verify oxygen delivery.

### Hypobaric Operation

The ventilator will operate normally at altitudes up to 15,000 feet. Changes in altitude will not affect pressure settings. However, delivered tidal volume increases and respiratory rate decreases with increasing altitude. This is due to lower barometric pressure than ventilator calibration at standard sea level.

To compensate for the effect of changing altitude on tidal volume and respiratory rate, use an external spirometer to verify tidal volume accuracy. Adjust the Tidal Volume and Respiratory Rate controls to the desired value as measured by the spirometer rather than the markings on the control panel.

### Disconnect Alarm

The ventilator has a patient circuit disconnect alarm system. This system cannot be turned off. If a circuit disconnect is sensed, the visual indicator on the front panel will illuminate and the audible alarm will sound.

The alarm will activate as soon as an oxygen source is turned on to the ventilator. You may silence the alarm for 1 minute by pressing the Reset / Silence button. Attaching the ventilator to a patient and starting ventilation will automatically reset the alarm system and turn off the audible and visual indicators.

A patient circuit disconnect is sensed when any of the following conditions occur:
*	Mandatory Breaths “ON” – circuit pressure does not rise above 15 cm H2O within 22 seconds of the last time at least 15 cm H2O was sensed.
*	Mandatory Breaths “OFF” – a pressure of less than 5 cm H2O is sensed for 22 seconds

The alarm system can be momentarily silenced by pressing the Reset / Silence button on the front panel. Pressing this button turns off the visual and audible indicators for 1 minute. Each time the Reset / Silence button is pressed, the alarm system restarts the 1 minute silence time delay. This delay is NOT cumulative. In other words, repeatedly pressing the Reset / Silence button will not increase the silence time by more than 1 minute.

## Section 5: Patient Circuit Adult / Pediatric Circuit
### Adult Circuit


The patient circuit designed for use with the PanVent TM Model A is part number 58001, 6 ft. disposable patient circuit. The compression volume is 1ml per cm H2O.

Additionally, a full range of compatible patient circuits are available to meet your needs. Other patient circuits may become available in the future. All acceptable circuits will ~have part numbers from 58001 to 58999.~

| PartNumber | Description |
| --- | --- |
| ~~58001~~ | 6ft.(1.8m)disposable,boxof15 |
| ~~58006~~ | 6ft.(1.8m)disposable,withexpiratoryfilter,boxof15 |
| ~~58011~~ | 6ft.(1.8m)disposable,withlargeadultmaskandheadstrap,boxof10 |
| ~~58021~~ | 6ft.(1.8m)disposable,withexpiratoryfilter,largeadultmaskandheadstrap,boxof10 |
| ~~58051~~ | 8ft.(2.4m)disposable,boxof15 |

 **WARNING:** Patient circuits other than the circuits listed above
may alter the ventilator's PEEP characteristics and / or expiratory flow resistance. They should NOT be
used and may lead to patient harm.

 **WARNING:** Air filters on the expiratory port of the patient
 circuit may alter the ventilator's PEEP characteristics and / or expiratory flow resistance. If the
  filter increases the flow resistance of the exhalation limb past 5 cm H2O/L/min, it should NOT be
   used and may lead to patient harm.

 **CAUTION:** The PanVent TM ventilator requires the use of a cuffed
 endotracheal tube for proper device operation.

#### VentilatorConnection

The patient circuit must be attached to the ventilator properly. Incorrect attachment could result in
 failure to provide adequate ventilation.

 The main breathing hose (22 mm) is connected to the “Patient Connection” port

 The small tubing (3 mm) connects the expiratory valve to the “Expiratory Valve” port

**NOTE:** The patient circuit is a single use, disposable device. Cleaning, reprocessing and / or reuse of this device is not recommended. The circuit and all components are sold clean and non-sterile.

## Single-Use only Medical Devices/Accessories

### How do I know if a device is Single-Use?


This symbol will be identified on the packaging and User’s Manual of the device.

### What does Single-Use mean?

Do not reuse. A single-use device is used on an individual patient during a procedure, such as pandemic
 ventilation, and then discarded. It is not intended to be reprocessed and used again, even on the same
  patient.

### What is the concern with reused device labeled Single- Use?
The use of reprocessed devices may present serious incidents relating to the health and safety of patients and healthcare professionals. Reuse can be unsafe because of risk of:

*	Cross-infection – inability to clean and decontaminate due to design, device components are not manufactured for disassembly and reassembly, especially for the SARS-CoV-2 virus

*	Endotoxin reaction – excessive bacterial breakdown products, which cannot be adequately removed by cleaning

*	Patient injury – device failure from reprocessing or reuse because of fatigue or material alteration

*	Chemical burns or sensitization – residues from chemical decontamination agents on materials that can absorb chemicals

 **NOTE:** If you reuse a single-use device you may be legally liable for the safe performance of the device.

# Section 6: Accessories

Using the PanVent TM Ventilator should be convenient and user-friendly for healthcare providers and
 patients.
Accessories for the device add serviceability in clinical situations and allow the device to adapt to
 the environment of use.

| Accessory | Image | Description |
| --- | --- | -- |
|Adult patient circuit |  | Disposable, single patient use. |
| | | 6 foot (1.8m) and 8 foot (2.4m) length|
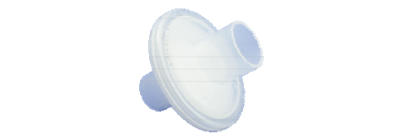
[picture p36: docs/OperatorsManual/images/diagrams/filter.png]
| Bacterial/Viral Filter |  | Disposable, sing patient uses.|
| | | Approved for use in in-line and on expiratory valve|
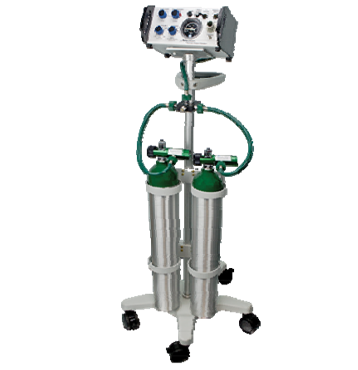
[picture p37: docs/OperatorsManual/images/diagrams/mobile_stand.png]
| MRI Compatible Mobile Stand |  | ~~3 foot, 9 inch (1.2m) tall~~|
||| ~~MRI compatible stand designed to hold the PanVent TM ventilator, model S or A. Two "E" size cylinders can be securely mounted on the stand. The ventilator attaches to the stand using a mounting plate, which allows the user to slide the ventilator on and off the stand for pandemic~~ |
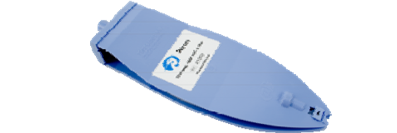
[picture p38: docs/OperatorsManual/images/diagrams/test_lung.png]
|Test Lung |  | A 1L or 3 L bag is ideal to test the device performance |
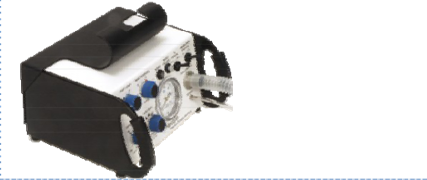
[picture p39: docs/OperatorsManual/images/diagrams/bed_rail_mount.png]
|Bed Rail Mount |  | ~~Allows for PanVent TM ventilator to hang from standard critical care bed rails~~|
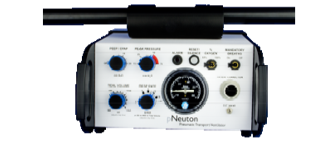
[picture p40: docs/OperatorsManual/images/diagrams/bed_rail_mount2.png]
|| | ~~Mount fits securely onto the top of the ventilator and provides a sturdy support during patient pandemic.~~|
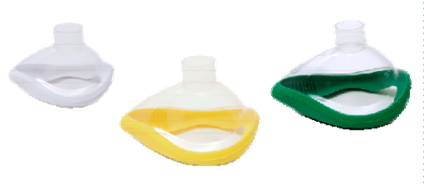
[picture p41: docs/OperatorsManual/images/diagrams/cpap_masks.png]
| Adult/Pediatric CPAP Masks |  | ~~Disposable, single patient use~~|
|||~~Adult Small~~|
|||~~Adult Medium~~|
||| ~~Adult Large~~|
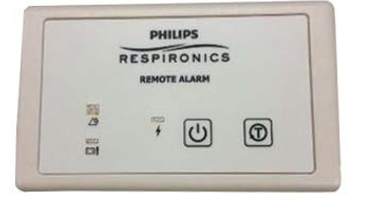
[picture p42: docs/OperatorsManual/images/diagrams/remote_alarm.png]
|Remote Alarm |  | ~Respironics Model 1118941~|
|||~Allows the user to attach a remote alarm to the PanVent TM Ventilator. Great for the MRI control room.~|
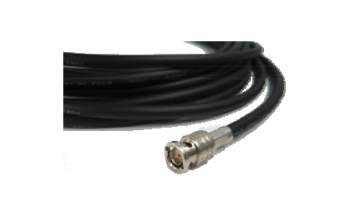
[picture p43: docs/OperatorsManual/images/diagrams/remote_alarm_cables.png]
| Remote Alarm Cables |  | ~MRI compatible BNC cables to attach the remote alarm to the PanVentTM Ventilator.~|
|||~50 foot (15 m) cable~|
|||~100 foot (30 m) cable~|
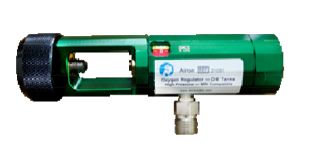
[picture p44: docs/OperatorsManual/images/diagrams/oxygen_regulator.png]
|Oxygen Regulator |  |  ~MRI compatible high pressure oxygen regulator for D / E size oxygen tanks~ |
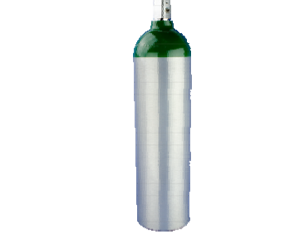
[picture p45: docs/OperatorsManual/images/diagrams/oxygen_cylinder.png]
|Oxygen Cylinder |  |E Size|
|||MRI compatible|
||| A 600 liter green oxygen cylinder with yoke stem valve|
|Reusable Patient Circuit |  | ~-	Adult/pediatric patient circuit, autoclavable~|
|||~1.8 meters (6 ft)~|
|||~**Available for International Customers Only.**~|

## Section 7: Theory of Operation

PanVent TM is a pneumatic ventilator based upon the Intermittent Mandatory Ventilation (IMV) principle. As such, adjustable respiratory rate and tidal volume breaths are delivered to the patient between which the patient may breathe spontaneously. This section describes how the ventilator operates.

Further information on the ventilator's theory of operation, including circuit diagrams, parts lists, and calibration instructions are available from CSSALT to properly trained service personnel.

### Pneumatic System

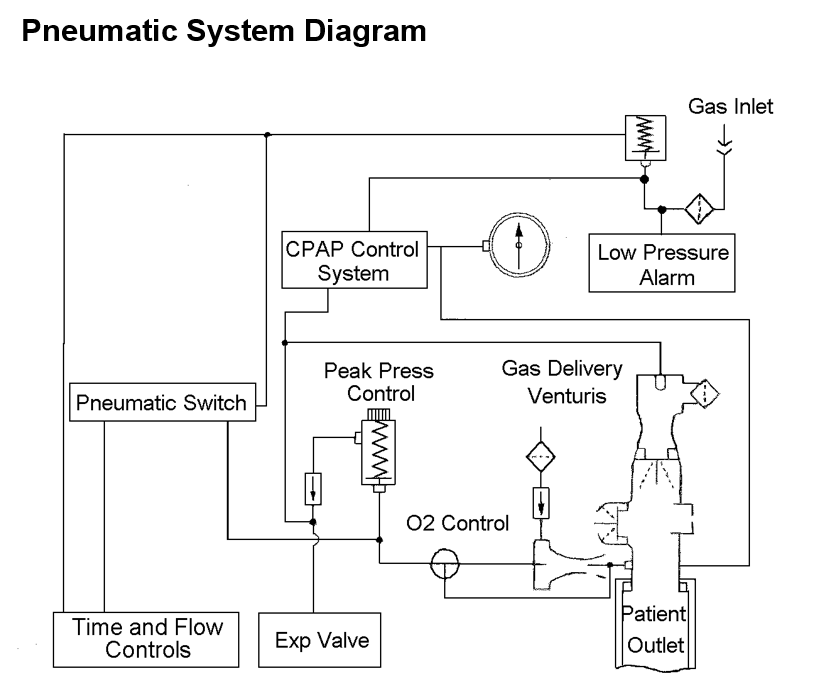
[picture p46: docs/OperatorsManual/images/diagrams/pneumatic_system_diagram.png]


#### Pneumatic System Description

The major components of the pneumatic system and the control of gas flow through the ventilator are as follows:
1.	High pressure gas (oxygen) enters the ventilator and is filtered (5 micron) and reduced to a lower working pressure (35 psi - 240 kPa).
1.	The timing circuit uses two precision control valves to control inspiratory and expiratory time. These valves charge (or reduce) pressure to a pneumatic timing cartridge. This timing cartridge turns on or off the ventilator's main flow valve.
1.	The main flow valve controls gas flow from the internal regulator to the % Oxygen control, which in turn delivers it to the patient. The % Oxygen control setting determines whether flow goes directly     to the patient or through the high flow venturi. If gas is directed to the patient, a restrictive orifice limits the flow to a specific flow rate (36 L/min). If gas is directed to the high flow venturi, ambient  air is entrained to provide precisely the same flow to the patient, but at a reduced FIO2 (approximately 65%). The high flow venturi provides stable performance (no stall) up to the maximum operating pressure (75 cm H2O) of the ventilator.
1.	The pressure generated by the main flow valve also powers the Peak Pressure control system. This system sends an adjustable pressure to the patient circuit expiratory valve. The pressure in this system determines the peak pressure that can be generated in the patient circuit.
1.	The adjustable PEEP / CPAP system directs a pressure signal to the expiratory valve to generate PEEP and provides flow on demand for spontaneous breaths.

#### Tidal Volume and Rate Control System

PanVent TM’s Tidal Volume and Respiratory Rate controls function to determine mandatory breath inspiratory and expiratory time.

Since the ventilator provides a fixed flow (at 36 L/min or 600 ml/sec) during a mandatory breath, setting a specific inspiratory time also sets a specific tidal volume. This tidal volume is so precise that the inspiratory time control is calibrated to reflect the range of tidal volumes available (360 to 1,500 ml).

The ventilator's tidal volume output will not change in the face of increasing patient circuit pressure. The only change that may occur to actual patient delivered tidal volume will be caused by compression of gas based upon the compliance of the patient circuit used. The compression volume of the ventilator itself is negligible.

The Respiratory Rate control adjusts expiratory time with a range 0.6 to 20 seconds. Rate is controlled by increasing or decreasing expiratory time. With a set tidal volume a slower respiratory rate will equate to a longer expiratory time. Tidal volume is not affected by changes to the Respiratory Rate control.

The Respiratory Rate control is calibrated for set tidal volumes between 500 and 900 ml. The calibrated

Respiratory Rate range optimizes the interdependence between the expiratory and inspiratory time for
 ease of operation. If the tidal volume is changed and the rate is not changed, the number of breaths
 that can occur in one minute changes.

For example:

    Volume=600,RespiratoryRate=12
      (I time=1sec, E time = 4 sec, total time = 5 sec)
    Change the volume to 900
      (I time changes to 1.5 sec)
    Resultant Respiratory Rate is now 11
      (total time for inspiration and expiration = 5.5 sec)

    Volume = 600, Respiratory Rate = 12
      (I time = 1 sec, E time=4sec, total time = 5 sec)
    Change the volume to 1200
      (I time changes to 2 sec)
    Resultant Respiratory Rate is now 10
      (total time for inspiration and expiration = 6 sec)

Tidal volumes below 500 ml will result in faster rates than marked on the Respiratory Rate control.
Tidal volumes higher than 900 ml will result in slower rates than marked on the Respiratory Rate
control. The marks on the Rate Control are wide to reflect the range of control position that will
provide the desired rate over the range of tidal volume. Always count the respiratory rate when first
placing the ventilator on a patient and whenever changing tidal volumes.

As when using any mechanical ventilator, careful attention to detail is required. It is suggested that
independent validation of tidal volume and rate be performed using external spirometers and timing
devices.

### Mandatory Breath Pressure Control System

During normal mandatory breath inspiration the expiratory valve functions to prevent gas from escaping through the expiratory valve. The pressure used to close the expiratory valve is set with the Peak Pressure control. The range is 15 to 75 cm H2O.

The Peak Pressure adjustment can be used to manipulate the highest pressure applied during mandatory breaths.
*	If volume limited ventilation is the goal, set the Tidal Volume control to the desired volume and the Peak Pressure control to at least 10 cm H2O above the pressure required to deliver that tidal volume.
*	If pressure limited ventilation is the goal, set the Tidal Volume control to the desired inspiratory time and the Peak Pressure control to the desired peak pressure.
During pressure limited ventilation any excess flow will be released by the expiratory valve while maintaining the desired peak pressure. This flow release may cause a "honking" sound as gas escapes through the partially closed valve.

The Peak Pressure control can be tested by occluding the patient port of the patient circuit during a mandatory breath. During the breath the pressure will rapidly rise to the set peak pressure. Turn the Peak Pressure control until the desired peak pressure is achieved.

### CPAP Demand Flow Breathing System

The ventilator's internal CPAP demand flow system provides gas for spontaneous breathing at adjustable
CPAP pressures up to 20 cm H2O. This system has several key features:

1.	When turned on, the system supplies a continuous flow of gas at approximately 10 L/min during the expiratory time of the ventilator. This flow of gas helps to establish the desired CPAP level by balancing flow with the pressure generated on the expiratory valve by the CPAP system.
1.	The continuous flow of gas also establishes the flow sensitivity to spontaneous breathing efforts. If the patient's inspiratory flow demand exceeds the continuous flow of gas, additional flow will be added to meet patient demand. There is no sensitivity adjustment to this system. The CPAP system will automatically meet the needs of the patient, greater than 100 L/min, by attempting to maintain the balance between flow and pressure at the expiratory valve.
1.	The PEEP control was evaluated to the dynamics of XXXX disposable patient circuit. Using this circuit will insure proper operation and the full 0 to 20 cm H2O PEEP range.

### Oxygen Delivery System

With the ventilator driven by 100% oxygen as the source gas, the ventilator can be set to deliver 65% or 100% oxygen. There are two independent systems within the ventilator that determine oxygen concentration. The following section describes how these systems operate.

#### Mandatory Breaths

The % Oxygen control determines the oxygen concentration of the mandatory breaths that enter the patient circuit at the Patient Connection. When set for 65%, an internal high flow venturi system entrains ambient air to decrease the FIO2 while maintaining the correct tidal volume. The high flow venturi provides stable performance up to the maximum operating pressure (75 cm H2O) of the ventilator.

#### Spontaneous Breaths

Spontaneous breaths are available from the internal CPAP system which uses a venturi mechanism separate from the mandatory breath high flow venturi. When turned on by the PEEP / CPAP control, the system delivers approximately 10 L/min baseline flow during the expiratory time of the ventilator.

The FIO2 of this system is set by the % Oxygen control. When set for 65%, the actual oxygen percentage
and baseline flow is related to the level of CPAP in use. Up to 10 cm H2O CPAP will provide a FIO2 of
approximately 0.65 +/- 0.10. As the CPAP level raises to 20 cm H2O, the FIO2 can be expected to
increase to as high as 0.75 +/- 0.10.This is due to a drop off in efficiency (stalling) of the CPAP
venturi system at higher CPAP levels. The actual FIO2 of spontaneous breaths will be approximately the
same as the baseline flow. Whether set for 65% or 100%, extremely high inspiratory flow demand may
decrease the desired FIO2.

*It is recommended that an external oxygen monitor be used at all times to measure and display the delivered oxygen concentration.*

 **WARNING:** Never operate the ventilator without proper oxygen gas supply at the required pressure.

#### Factors Effecting the Operating Time of Oxygen Tanks
There are several factors that affect the length of time the ventilator will operate from a tank of oxygen. The ventilator uses very little gas for its own operation (less than 4 L/min) and is not a major factor in oxygen tank consumption. The major factors are:

* Volume of oxygen in the tank
* Patient's tidal volume and rate
* Position of the % Oxygen control
* If the PEEP/CPAP system is on or off

Setting the % Oxygen control to 65% will decrease the amount of oxygen used from the tank, nearly doubling the time an oxygen tank lasts.

**NOTE:** Always use full oxygen and air tanks before the start of any pandemic. The calculation of any
expected run time becomes unreliable as tank pressure is reduced.

#### Example of expected operating time using a full "E" size cylinder (660 liters) PEEP/CPAP off

|Minute Volume|100% Oxygen|65%Oxygen|
| -- | -- | -- |
|5 l/m | 77 min | 80 min |
|10l/m | 40min | 76min |
|15 l/m | 33min | 60min |

The PEEP / CPAP system, when turned on, uses approximately 5 L/min oxygen from the tank to provide the 10 L/min baseline flow of the system. The patient's own spontaneous tidal volume and rate will use additional oxygen from the tank, based upon the tidal volume of those breaths.

#### Example of expected operating time using a full "E" size cylinder (660 liters) PEEP/CPAP on

| Minute Volume | 100% Oxygen | 65% Oxygen |
| --- | --- | --- |
| 5l/m | 29min | 37min |
| 10l/m | 26min | 33min |
| 15l/m | 23min | 30min |

used. In addition, safe MRI practice calls for all devices used in the proximity of a MRI scanner be anchored to prevent inadvertent movement.

### MRI Compatibility

The ventilator was engineered and built to be MRI compatible. Testing in a MRI scanner has shown
that the scanner does not affect the ventilator's performance. The ventilator does not generate artifact, RF noise, or other deleterious effects on the operation of the MRI scanner or it's production
of an image. In addition, due to PanVent TM Ventilator components, heating of the ventilator does not
occur during scanning.

Testing for MRI compatibility was done following ASTM MRI safetystandards F2052–06e1 and F2119–07. The
MRI scanner used has the following maximum performance levels:

* Static field strength-3Tesla
* Spatial field gradient-720G/cm

The scanner used for testing was an active shielded system. The ventilator was placed in the position
of maximum field strength and maximum spatial gradient. The standard patient
circuit(Aironpartnumber58031) was used. A standard imaging sequence with a maximum scanning time of 5
minutes was used.

**TODO: Retrieve image**:w
The PanVent TM Ventilator meets testing requirements for use within the Magnetic Resonance Environment
with a conditional marking for safety.

**NOTE:** Airon recommends that users perform the above referenced tests in their MRI scanner prior to
patient use.

 **WARNING:** While tests show that the ventilator functions at the
bore of the MRI unit, Airon Corporation does not recommend that the ventilator be clinically used at or
with in the bore of MRI scanners. A minimum proximity of 12 inches(0.3meter) from the bore should be
used. In addition, safe MRI practice calls for all devices used in the proximity of a MRI scanner be
anchored to prevent in advertent movement.

### Disconnect Alarm

The ventilator has an internal patient circuit disconnect alarm system. This system cannot be turned off. If a circuit disconnect is sensed, the visual indicator on the front panel will illuminate and the audible alarm will sound.

The alarm will activate as soon as an oxygen source is turned on to the ventilator. Attaching the ventilator to a patient and starting ventilation will automatically reset the alarm system and turn off the audible and visual indicators

The alarm system can be momentarily silenced by pressing the Reset / Silence button on the front panel. Pressing this button turns off the visual and audible indicators for 1 minute. Each time the Reset / Silence button is pressed, the alarm system restarts the 1 minute silence time delay. This delay is NOT cumulative. In other words, repeatably pressing the Reset / Silence button will not increase the silence time by more than 1 minute.

The alarm system is entirely pneumatic and uses no electricity. A series of valves and pneumatic capacitances provide the sensing network. Two subsystems are used, one for when Mandatory Breaths are turned on and another for when Mandatory Breaths are turned off. This allows  the alarm to operate when only CPAP is functioning. Due  to the nature of this system, a minimum CPAP of 5 cm  H2O is required. If CPAP is set for less than 5 cm H2O and Mandatory Breaths are not turned on, the alarm system will activate.

The alarm system provides a passive, non-electrically charged remote alarm output on the rear of the ventilator.

### Low Gas Supply Alarm

The Low Gas Supply Alarm will occur if the driving gas supply drops below safe levels (30 psi, 200 kPa). The alarm activates as long as driving gas is available or until the supply pressure returns to normal.

When operating from an oxygen cylinder the ventilator will gradually use up the gas in the cylinder and tank pressure will fall. Once the cylinder pressure reaches approximately 500 psi, most portable tank regulators will start to decrease pressure to the ventilator during mandatory breaths. As this happens that Low Gas Supply Alarm will sense the decreased pressure and begin to intermittently alarm each time the pressure drops during inspiration. As pressure in the cylinder falls to lower values, the amount of time the regulator is delivering low pressure increases and the alarm sounds longer. Eventually the regulator is unable to maintain pressure and the alarm will sound continuously until all gas in the cylinder is used.

 **WARNING:** The Low Gas Supply Alarm will only activate for a very
short period of time if the gas supply abruptly ceases. This can occur if operating from a wall source
and the gas supply hose is disconnected from the gas supply outlet. In fact, the Low Gas Supply Alarm
may not sound at all when the ventilator is disconnected from a wall source. This is because all gas in
the high pressure hose immediately exits out from where the hose was connected to the outlet and there
is no gas pressure to power the ventilator’s alarm. When using the ventilator on a patient always
insure that the supply gas is secure and operating at the proper pressure.

## Section 8: Troubleshooting

This troubleshooting guide lists common problems that may be encountered and possible solutions. If none of the corrective actions seem to work, contact CSSALT or your distributor.

| **Indication** | **Meaning** | **Corrective**** Action** |
| --- | --- | --- |
|Ventilator does not operate – no patient ventilation| Missing or insufficient driving gas supply | Check gas source, 55 psi (380 kPa) at 40 L/min is required |
||Patient circuit disconnection | Reconnect patient circuit |
||Internal malfunction| Send ventilator for service|
|Ventilator seems to “want” to operate, but no breaths are generated| Peak Pressure control set too low |Increase Peak Pressure control|
||Respiratory Rate set too low	|Increase Respiratory Rate
|| Expiratory valve drive line disconnected | Insure tubing is properly connected | Expiratory Valve is malfunctioning	Replace patient circuit|
||Insufficient driving gas supply	| Check gas source, 55 psi (380 kPa) at 40 L/min is required|
||Internal malfunction	| Send ventilator for service|
|Ventilator appears to be stuck in inspiration	|CPAP may be turned on high	| Check CPAP control|
||Internal malfunction | Send ventilator for service
|Ventilator stops and starts | Insufficient driving gas supply | Check gas source, 55 psi (380 kPa) at 40 L/min is required|
|Lower minute volume than desired |	Insufficient driving gas supply |	Check gas source, 55 psi (380 kPa) at 40 L/min is required|
||Leak in the Patient Circuit or Expiratory Valve	| Replace patient circuit|
||Obstruction of gas output	| Check or replace patient circuit|
||Use in hyperbaric condition |	Ventilator should not be used in hyperbaric conditions|
|| Tidal volume control out of calibration | Send ventilator for service|
||Internal malfunction | Send ventilator for service|
|Higher minute volume then desired | Use at higher altitude then calibration | Use external spirometer to verify tidal volume|
||Tidal volume control out of calibration |	Send ventilator for service |
||Internal malfunction | Send ventilator for service|
|Higher minute volume then desired|	Use at higher altitude then calibration|	Use external spirometer| to verify tidal volume|
||Tidal volume control out of calibration |	Send ventilator for service|
||Internal malfunction	|Send ventilator for service|
|Tidal volume inaccurate	|Leak in the patient ET-Tube, mask, breathing circuit or expiratory valve|	Check patient interface.| Replace patient circuit if at fault|
||	Ventilator is operating at an altitude different then calibration	|Tidal volume should be measured by an external spirometer|
||	Tidal volume control out of cal |	Send ventilator for service|
| Rate control inaccurate | Tidal volume set below 500 ml or above 900 ml | This is normal. Rate will be faster when tidal volume is set lower than 500 ml. Rate will be slower when tidal volume is set higher than 900 ml|
||Rate control out of cal |	Send ventilator for service|
|Patient pressure too high|	Tidal Volume set too high|	Decrease Tidal Volume or Peak Pressure setting|
||Patient response	|ET-Tube may be occluded or patient may be biting tube|
||Expiratory Valve malfunctioning|	Replace patient circuit|
||Internal malfunction| Send ventilator for service|
|Can’t get the PEEP / CPAP desired |Expiratory Valve malfunctioning|	Replace patient circuit|
||	Using a circuit not recommended by CSSALT|	Replace patient circuit|
||	Internal malfunction|	Send ventilator for service|
||	Excessive “chattering” of CPAP system|	Occurs when using some test lungs but will not when connected to a patient. If problem persists, send ventilator for service|
|Ventilator using too much gas	PEEP / CPAP| system turned “on”	| Turn off PEEP / CPAP system|
||	Leak at source gas |	Check hoses and tank regulator for leaks|
||	Internal leaks|	Send ventilator for service|
|Oxygen concentration too low|	Source gas not 100% oxygen|	Insure source gas is 100% oxygen|
||	High patient spontaneous ventilation |	Decrease spontaneous ventilation|
||	Internal malfunction	|Send ventilator for service|
|Alarm activated|	Patient circuit disconnection|	Reattach circuit or locate leak|
||	Alarms at start-up when gas is supplied to ventilator|	Normal operation. To silence alarm, attach patient (or test lung) or press Reset| Silence button
||	Expiratory valve tubing disconnected | Insure tubing is connected properly|
|| Leak in the Patient Circuit or Expiratory Valve|	Replace patient circuit|
||Insufficient driving gas supply – alarm sounds briefly during each mandatory breath|	Tank may be low. Check gas source, 55 psi (380 kPa) at 40 L/min is required|
|| Mandatory Breaths OFF and CPAP set to less than 5 cm H2O	| Set CPAP to at least 5 cm H2O or Mandatory Breaths ON |
|Excessive patient effort	If peak pressure does not reach 15 cm H2O due to patient insp effort during mandatory breaths, alarm will sound. This is normal operation|
||Internal malfunction	|Send ventilator for service|
|Alarm does NOT activate|	Patient circuit occluded	Check circuit|
||	Expiratory valve drive line kinked or occluded |	Check / replace patient circuit|
||Internal malfunction	|Send ventilator for service|
|Visual alarm activates but audible does not| Reed Cap Malfunction|	Replace reed cap on back of unit|

## Section9: Cleaning and Maintenance

### Cleaning the Ventilator

*	Use only mild detergent or disinfectant and water with a soft cloth.
*	Do not immerse the ventilator in water.
*	Do not attempt to sterilize the ventilator with autoclave or ethylene oxide. Severe damage to the ventilator may occur.

#### Cleaning / Disinfecting the Patient Circuit
The patient circuit is a disposable, single use device. This circuit must not be cleaned, disinfected or reused.

See Single-Use only Medical Device information.

#### RoutineMaintenance

CSSALT recommends that an Operational Verification Test (see Section 4) be performed at initial installation and prior to use on each patient. Institution’s standards may require additional biomedical surveillance. No additional routine maintenance is required.

 **Factory Preventative Maintenance**

 *	Ventilator service is required every 2 years to ensure continuous safety and reliability of the ventilator.
 *	Ventilator service includes:
    * Replacement of internal filters
    * Replacement of internal materials subject to wear
    * Reconditioning of the enclosure
    * Complete calibration
 *	This service must only be performed by approved service technicians.
 *	Failure to perform this service may result in malfunctioning of the ventilator.

## Section 10: Specifications

### General Description
*	Pneumatically operated ventilator provides automatic mechanical ventilation with a built-in PEEP / CPAP demand flow system for spontaneous breathing
*	Patient ranges: pediatric to adult, > 23 kg.
*	Equipment not suitable for use in the presence of flammable anesthetics
*	Rated for continuous operation

### VentilatorSystemPerformance

|	Controls | limitations |
|--|--|
|Mandatory Breaths	 | On or Off
| Respiratory Rate	  |from 3 to 50 bpm
|	Tidal Volume	      |from 360 to 1,500 ml
| Peak Pressure	      |from 15 to 75 cm H2O
|	PEEP / CPAP		      |from 0 to 20 cm H2O
|	% Oxygen		        |100% or 65%

|Operating Ranges | |
|--|--|
| Inspiratory Time | 0.6 to 2.5 seconds |
| Expiratory Time | 0.6 to 20.0 seconds |
| Minute Volume | 0.2 to 30 L/min |
| Flow Pattern  | square,36L/min |
| Internal P Limit | 80cmH2O |

|Accuracy of Controls| |
|--|--|
|Respiratory Rate | +/- 10%(VTbetween500-900)|
|Tidal Volume | +/-10% |
|Peak Pressure | +/-10%|
| PEEP/CPAP | +/-5%|
| FIO2, mandatory breaths | +/- 10%|

| Precision-breath to breath repeatability of controls | |
|--|--|
| Respiratory Rate | +/-10%|
| Tidal Volume | +/-25ml |
| Peak Pressure | +/-5cm H2O |
| PEEP/CPAP | +/-2cmH2O |
| FIO2 | +/-5%|

|Specificity-effect of one control on another ||
|--|--|
|Respiratory Rate - if tidal volume is constant | +/-5%|
|Tidal Volume | +/-5% |
|Peak Pressure | +/-5% |
|PEEP/CPAP | +/-5%|
| FIO2 | +/-5%|

|Internal Compliance | 0.1ml/cmH2O|
|--|--|

| Ventilator Resistance to Flow | |
|--|--|
| Inspiratory, 60L/min | lessthen2cmH2O/l/sec |
| Expiratory,50L/min | lessthen2cmH2O/l/sec |

### Alarm System

* Patient Disconnect
  * Pressure:
    * mandatory breath OFF, less than 5 cmH2O
    * mandatory breath ON, less than 15 cmH2O
  * Alarm delay: 22 seconds
  * Alarm silence: 60 seconds

* Low Gas Supply
  * Input supply pressure: less than 30psi (2.1bar)
  * Cannot be silenced

### Environmental and Physical Characteristics

* MRI Conditional. Tested with a scanner up to:
  *	Maximum static field strength - 3 T
  *	Maximum spatial field gradient - 720 G/cm

* Hypobaric (high altitude) compatible up to 15,000 feet
* Weight and Size: 6.5 pounds (3 kg), 5.0"H x 10.0"W x 7.3"D (12.7 cm x 25.4 cm x 18.5 cm)
* Storage Temperature Range: -20 to 60 °C (-4 to 140°F), 15 to 95 percent humidity, noncondensing

### PowerSources

*	Driving gas requirement
  *	55 psi + 15 psi (380 kPa + 100 kPa)
  *	100% oxygen. Do not use the ventilator with other types of gases.
  *	The gas supply must be capable of delivering at least 40 liters per minute at 55 psi. If input pressure drops less than 30 psi due to insufficient gas flow, the ventilator will alarm and begin to malfunction.

**NOTE:** Driving gas consumption at 10 L/min minute volume;
*	PEEP / CPAP off: 4 L/min
*	PEEP / CPAP on, 65%: 9 L/min
*	PEEP / CPAP on, 100%: 15 L/min

## Section 11: Limited Warranty

CSSALT, through its Official Distributor, warrants this product to be free from defects in construction, material and workmanship for a period of twelve (12) months from the date of original delivery to buyer when operated properly under conditions of normal use for which the product is intended. This twelve (12) month warranty does not extend to expendable items such as membranes, hoses, patient circuits and filters which are warranted to be free of defects only at time of original delivery.

The official CSSALT Distributor will, at its option, either repair or replace any defective product, as above defined, which is reported to that CSSALT Distributor within 72 hours of occurrence during the warranty period. If so instructed by the Distributor, such defective products must be returned to the official CSSALT Distributor in the original container with freight charges prepaid. In any case, the CSSALT Distributor shall be responsible for repairs to, or replacement of, such defective product only.

### LIMITATIONS ON AND DISCLAIMER OF WARRANTIES:
CSSALT and its CSSALT Distributors shall be relieved of any liability under this warranty: if the product is not used in accordance with manufacturer's instructions; if attachment or incorporation of any device is made to this product without written approval; if use is made in any manner other than intended by the manufacturer; if regular periodic maintenance and service is not performed; if repairs are made by other than authorized service personnel; if the product has been subject to abuse, misuse, negligence or accident. Any product that has been mechanically or electronically altered without specific written authorization from CSSALT is also excluded from this warranty.

The warranty described in this Agreement is in lieu of all other warranties. THE PARTIES AGREE THAT THE IMPLIED WARRANTIES OF MERCHANTABILITY AND FITNESS FOR A PARTICULAR PURPOSE AND ALL OTHER WARRANTIES, EXPRESS OR IMPLIED, ARE EXCLUDED FROM THIS AGREEMENT.

Except as stated above, CSSALT or its Distributors  SHALL NOT BE LIABLE FOR ANY DAMAGES, CLAIMS OR LIABILITIES INCLUDING, BUT NOT LIMITED TO, PERSONAL BODILY INJURY, OR INCIDENTAL, CONSEQUENTIAL, and OR SPECIAL DAMAGES.

## Section12:Index

### A
* Accessories 6-1
* Administering Oxygen 7-6
* Airway Connection Port 3-3
#### Alarms:
  * High Pressure 3-5
  * Low Gas Supply 3-6, 7-11, 10-2
  * Patient Disconnect 3-7, 4-5, 7-10, 10-2
* Altitude Operation 2-4, 4-5
* Anti-Suffocation System 3-6
### C
* Cautions 2-3
#### Circuit, Patient Breathing:
  * Cleaning 9-1
  * Configuration 5-1
  * Connecting 5-2
#### Cleaning:
  * Patient Breathing Circuit 9-1 Ventilator 9-1
* Contraindications 2-6
#### Controls:
  * % Oxygen 3-2
  * Peak Pressure 3-1
  * PEEP / CPAP 3-2
  * Respiratory Rate 3-2
  * Tidal Volume 3-2
* Continuous Flow - CPAP 7-5
#### CPAP:
  * Control 3-1
  * Functional Operation 7-5
  * Trigger Sensitivity 7-6
### E
#### Expiratory Valve:
  * Connection 3-3, 5-2
  * Relationship to PEEP/CPAP System 7-6
### F
* Front Panel 3-1
### H
* High Altitude Operation 4-5
* HighPressureAlarm3-7
* HyperbaricOperation2-2
* HypobaricOperation4-5
### I
* Indications For Use 2-6
* Internal Patient Safety Systems 3-6
* Interrelationship Between Volume & Rate Controls 4-4,7-3
### L
* Low Gas Supply Alarm 3-6,7-11
### M
* Maintenance-Ventilator Service 9-1
#### Mandatory Breaths:
  * FIO2 4-5
  * Flow Rate 6-3
  * Interrelationship Between Volume & Rate Controls 6-3
* Medical Symbol Key 2-7
* Mode of Operation 2-5, 6-1
* MRI Compatibility 7-9, 10-2
### N
* Notes 2-4
### O
* Operational Verification 4-2
#### Oxygen:
  * % Oxygen Control 3-2
  * Driving Gas Inlet 3-4
  * Driving Supply Requirements 10-3
  * Operational Characteristics 7-6
  * Tank, Expected Operating Time 7-7
### P
* Patient Circuit Cleaning 9-1
  * Configuration 5-1
  * Connecting 5-2
  * Disconnect Alarm 3-7, 4-5
  * Single Use 5-3
* Patient Ventilation 4-3
* Peak Pressure Control 3-1
* Performance Verification 4-2
#### PEEP/CPAP:
  * Control 3-2
  * Functional Operation 7-5
  * Trigger Sensitivity 7-6
* Pneumatic System 7-2
* Pneumatic Low Gas Supply Alarm 3-6
#### Power Requirements:
  * DrivingGasSupply10-3
#### Pressure:
  * Peak Pressure Control 3-1
  * PEEP/CPAP Control 3-2
* Pressure Gauge 3-1
* Preventative Maintenance 9-1
#### Principles of Operation:
  * CPAP Demand Flow Breathing System 7-6
  * Mandatory Breath Pressure Control System 7-5
  * Oxygen Delivery System 7-6
  * Pneumatic System Diagram 7-1
  * Pneumatic System Description 7-2
  * Tidal Volume and Rate Control System 7-3
### R
* Rear Panel 3-3
#### Respiratory Rate:
  * Control 3-2
  * Interrelationship Between Volume & RateControls 4-4,7-3
### S
* Safety Systems 3-6
* Sensitivity 7-6
* Set Up 4-1
* Service, Preventative Maintenance 9-1
Single-Use only Devices/Accessories 5-3
#### Specifications:
  * AlarmSystem10-2
  * Environmental and Physical Characteristics 10-3
  * General Description 10-1
  * Power Sources 10-3
  * Ventilator System Performance 10-1
#### Spontaneous Breaths
  * FIO2 7-7
### T
#### Tidal Volume:
  * Control3-2
  * Interrelationship Between Volume & Rate Controls 7-3
#### Theory of Operation:
  * CPAP Demand Flow Breathing System 7-5
  * Mandatory Breath Pressure Control System 7-5
  * Oxygen Delivery System 7-6
  * Pneumatic System Diagram 7-1
  * Pneumatic System Description 7-2
  * Tidal Volume and Rate Control System 7-3
  * Trouble shooting Ventilator 8-1
### U
* Unique Device Identifier (UDI) 3-5
### V
* Ventilator Set-up 4-1
* Verification, Operational 4-2
### W
* Warnings 2-1

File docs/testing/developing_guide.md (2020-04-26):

---
layout: default
title: Development / Testing Guide
---

# Development and Testing Guide

## What you need to know

If you are a developer, here is what you need to know about changing code:

* The github is where all code lives and how code is to be distributed

* All official code lives on the master branch of the github.

* Every time changes are requested to be merged onto master (always via a pull request), a formal testing report must be included.

* All code to be merged to master must undergo and pass a review by a fellow collaborator.

* Any branch to be merged onto master needs to be up to date. ie: all commits of the non-master branch must be made on top of the most recent commits on master. This is a practice know as [rebasing](https://git-scm.com/book/en/v2/Git-Branching-Rebasing), and it will give us a nice code base histroy moving forward.

## Actually Developing

### Get the most recent code that works

You must first get the most recent code that works.

* Clone the repo

`git clone git@github.com:CSSALTlab/Open_Source_Ventilator.git`

*NOTE: if you have already cloned the repo, you do not need to do this*

* Navigate to the root of the repo

*NOTE: if you just cloned you can use* `cd Open_Source_Ventilator`

* Fetch the repository's branches (this download will suffix remote branches with `origin/` so your local branches are safe.)

`git fetch origin`

* Checkout your local master branch

`git checkout master`

* Reset your local version of the master branch to match what is on the github

**NOTE: This will delete all diffrences between your local master branch and the remote master branch.**

`git reset origin/master --hard`

### Making changes

* Checkout a new branch

`git checkout -b <my-branch-name>`

* Make some changes to the code testing along the way

* Once you are pleased with your changes

* Review your changes

  * Get a list of exatly the files that you changed

`git status`

  * See exactly how you changed those files

`git diff`

* Add all the files you changed

  `git add <file-names>`

* Make sure you are not on the master branch

`git status`

  * If you are on the master branch

`git checkout -b <my-branch name>`

* Commit your changes to your current branch with a message about what you did

`git commit -m "<i-fixed-bug-x>"`

* STOP EDITING CODE FILES

### Conduct a Full Formal Test

**NOTE: Before conducting a test, make sure your code is uptodate with master with** `git rebase master` **make sure to resolve any merge conflicts and do some more informal tests to make sure your code does indeed work as you think it should.**

* make sure you are not still in the middle of a merge / rebase with

`git status`

* Go go thourgh and test all functions listed in out [Testing Report](./blank_testing_doc.html) Filling in the boxes as you go.
**NOTE Do not refresh the page, it will delete all yourt entered values**

* If you want to add a test / change the testing report document
  * edit the testing document source file under `docs/testing/blank_testing_doc.md` to reflect the new test. 
  * Make sure to follow the steps from the [guide on adding documentation](../AddingDocumentation.html)

**NOTE: make sure to include the changes to the documentation on this branch. ie: do not checkout a separate branch for editing documentation in this instance, since the change in documentation is to go with the changes in the code already commited on this branch** 

  * Once you are happy with the changes to the testing report, commit them with

`git add <path-to-testing-report>`

`git commit -m "<i-added-x-to-testing-report>"`

  * launch the local jekyll server (instructions ini the [guide on adding documentation](../AddingDocumentation.html))

  * fill out the fillable text docs on the Blank Testing Report page from the local jekyll server (so your added tests show up)

  * download the site as html into your downloads folder

  * kill the jekyll server with `Ctrl + c`

* If you do not want to change the testing document

  * see the [blank testing report](./blank_testing_report_doc.md)

  * fill out the text boxes with your test results

  * download the webpage as html

  * add the testing report in markdown format under `docs/tests/`

  * Commit the test to this branch

`git add <path-to-my-test>`

`git commit -m <executed-test-x>`

### Request your changes be added to master branch

This is known in the business as a `Pull Request`

* push your local development branch to the github
**NOTE: make sure you are not on master branch with** `git status`

`git push origin <my-branch-name> -u`

* go to [the github](https://github.com/CSSALTlab/Open_Source_Ventilator)

* click on `Pull Requests`

* click `New Pull Request`

* select your branch under the compare tab

* select someone to review your propsed changes to double check your work. (Nessesary even after a foormal test)

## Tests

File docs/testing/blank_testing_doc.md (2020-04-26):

---
layout: default
title: Blank Testing Report
---
This is a black testing report we host for developers to fill out when they are
proposing updating the code on master.

# Testing Report

|Date|Version|Revision|
|--|--|--|
|<textarea rows="1" cols="20" wrap="hard"> | <textarea rows="1" cols="20" wrap="hard"> | <textarea rows="1" cols="40" wrap="hard">|

Date: <textarea rows="1" cols="20" wrap="hard">

Test Evaluator: <textarea rows="1" cols="20" wrap="hard">

|Item |Description |Result |Comment|
|--|--|--|--|
|1.| Software being evaluated. Include version, author, date,| <textarea rows="2" cols="25" wrap="hard">|<textarea rows="2" cols="25" wrap="hard">|
|2| Compile outcome| <textarea rows="2" cols="25" wrap="hard">|<textarea rows="2" cols="25" wrap="hard">|
|3| % of program space | <textarea rows="2" cols="25" wrap="hard">|<textarea rows="2" cols="25" wrap="hard">|
|4| % of dynamic memory | <textarea rows="2" cols="25" wrap="hard">|<textarea rows="2" cols="25" wrap="hard">|
|5| Zero’ing of airway pressure sensor| <textarea rows="2" cols="25" wrap="hard">|<textarea rows="2" cols="25" wrap="hard">|
|6| Zero’ing of flow measurement system| <textarea rows="2" cols="25" wrap="hard">|<textarea rows="2" cols="25" wrap="hard">|
|7| Ability to re-zero during later operation| <textarea rows="2" cols="25" wrap="hard">|<textarea rows="2" cols="25" wrap="hard">|
|8| Protection from accidentally turning Ventilator OFF | <textarea rows="2" cols="25" wrap="hard">|<textarea rows="2" cols="25" wrap="hard">|
|9| Display of Chosen Respiratory Rate| <textarea rows="2" cols="25" wrap="hard">|<textarea rows="2" cols="25" wrap="hard">|
|9B| RR selectable | <textarea rows="2" cols="25" wrap="hard">|<textarea rows="2" cols="25" wrap="hard">|
|10| Display of Chosen I:E Ratio| <textarea rows="2" cols="25" wrap="hard">|<textarea rows="2" cols="25" wrap="hard">|
|10B| I:E at least 1:1 1:2 1:3 | <textarea rows="2" cols="25" wrap="hard">|<textarea rows="2" cols="25" wrap="hard">|
|11| Display of Chosen Peak Pressure Limit|  <textarea rows="2" cols="25" wrap="hard">|<textarea rows="2" cols="25" wrap="hard">|
|12| Display of Chosen Flow Limits(upper lower or otherwise)| <textarea rows="2" cols="25" wrap="hard">|<textarea rows="2" cols="25" wrap="hard">|
|13| Display of airway pressure observed| <textarea rows="2" cols="25" wrap="hard">|<textarea rows="2" cols="25" wrap="hard">|
|13B| Display of PEEP| <textarea rows="2" cols="25" wrap="hard">|<textarea rows="2" cols="25" wrap="hard">|
|14| Display of flow measured | <textarea rows="2" cols="25" wrap="hard">|<textarea rows="2" cols="25" wrap="hard">|
|15| Low pressure alarm| <textarea rows="2" cols="25" wrap="hard">|<textarea rows="2" cols="25" wrap="hard">|
|16| High Pressure alarm| <textarea rows="2" cols="25" wrap="hard">|<textarea rows="2" cols="25" wrap="hard">|
|17| Stop inspiration at high pressure alarm|  <textarea rows="2" cols="25" wrap="hard">|<textarea rows="2" cols="25" wrap="hard">|
|18| Open expiratory valve at high pressure alarm| <textarea rows="2" cols="25" wrap="hard">|<textarea rows="2" cols="25" wrap="hard">|
|19| Alarm for low flow volume| <textarea rows="2" cols="25" wrap="hard">|<textarea rows="2" cols="25" wrap="hard">|
|20| Alarm for high flow volume| <textarea rows="2" cols="25" wrap="hard">|<textarea rows="2" cols="25" wrap="hard">|
|21-29 Reserved||||
|30| Alarm Temporary Silence| <textarea rows="2" cols="25" wrap="hard">|<textarea rows="2" cols="25" wrap="hard">|
|31| Inspiratory Pause Enable| <textarea rows="2" cols="25" wrap="hard">|<textarea rows="2" cols="25" wrap="hard">|
|32| Inspiratory Pause Disable| <textarea rows="2" cols="25" wrap="hard">|<textarea rows="2" cols="25" wrap="hard">|
|33| Assist Ventilation Enable|  <textarea rows="2" cols="25" wrap="hard">|<textarea rows="2" cols="25" wrap="hard">|
|34| Assist Ventilation Disable | <textarea rows="2" cols="25" wrap="hard">|<textarea rows="2" cols="25" wrap="hard">|
|35| Trigger for Assist Ventilation | <textarea rows="2" cols="25" wrap="hard">|<textarea rows="2" cols="25" wrap="hard">|
|36| Delay from trigger to effective inspiratory assistance| <textarea rows="2" cols="25" wrap="hard">|<textarea rows="2" cols="25" wrap="hard">|
|40| Failure if button held down |  <textarea rows="2" cols="25" wrap="hard">|<textarea rows="2" cols="25" wrap="hard">|
|41| Outcome of random simultaneous button presses|  <textarea rows="2" cols="25" wrap="hard">|<textarea rows="2" cols="25" wrap="hard">|
|42| Outcome of pulling power |  <textarea rows="2" cols="25" wrap="hard">|<textarea rows="2" cols="25" wrap="hard">|
|43| Outcome of pulling BMP280 clock line|  <textarea rows="2" cols="25" wrap="hard">|<textarea rows="2" cols="25" wrap="hard">|
|44| Outcome of pulling BMP280 data line| <textarea rows="2" cols="25" wrap="hard">|<textarea rows="2" cols="25" wrap="hard">|
|45| Outcome of pulling BMP280 Vin line| <textarea rows="2" cols="25" wrap="hard">|<textarea rows="2" cols="25" wrap="hard">|
|46| Function of ventilator with missing BMP280glue (cold start)| <textarea rows="2" cols="25" wrap="hard">|<textarea rows="2" cols="25" wrap="hard">|
|47| Technique to re-enable BMP280| <textarea rows="2" cols="25" wrap="hard">|<textarea rows="2" cols="25" wrap="hard">|
|48| Outcome of attempting to re-enable BMP| <textarea rows="2" cols="25" wrap="hard">|<textarea rows="2" cols="25" wrap="hard">|
|49-50 Reserved||
|50| Measured RR @ setting 10| <textarea rows="2" cols="25" wrap="hard">|<textarea rows="2" cols="25" wrap="hard">|
|51| Measured RR @ setting 30|  <textarea rows="2" cols="25" wrap="hard">|<textarea rows="2" cols="25" wrap="hard">|
|52| Measure of idle time of processor|  <textarea rows="2" cols="25" wrap="hard">|<textarea rows="2" cols="25" wrap="hard">|
|53| Active PEEP| <textarea rows="2" cols="25" wrap="hard">|<textarea rows="2" cols="25" wrap="hard">|
|54| Assist Vent| <textarea rows="2" cols="25" wrap="hard">|<textarea rows="2" cols="25" wrap="hard">|

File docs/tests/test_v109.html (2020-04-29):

Open Source Ventilator Project (https://cssaltlab.github.io/Open_Source_Ventilator/)

This is a black testing report we host for developers to fill out when they are proposing updating the code on master.

# Testing Report

Date | Version | Revision
4/29/2020 | 1.09

Date: 0429 0227ED

Test Evaluator: G. Gibby

Item | Description | Result | Comment
1. | Software being evaluated. Include version, author, date, | Version 109Ashhar1.0/Gibby0429
2 | Compile outcome | Small number of warnings for variables not utilized | No errors of any kind.
3 | % of program space | 22536=73% of space | Plenty of room.
4 | % of dynamic memory | 1049 = 51% , 999 free | Plenty of room.
5 | Zero’ing of airway pressure sensor | Yes, announced by dot dot dash tones ending in 1000 Hzdash | Can be rezeroed with menu option at will
6 | Zero’ing of flow measurement system | Yes, same as (5)
7 | Ability to re-zero during later operation | Yes, with tones supported
8 | Protection from accidentally turning Ventilator OFF | (battery backup) – two step process requires confirmationin menu structure
9 | Display of Chosen Respiratory Rate | YES - “ticker”
9B | RR selectable | YES – menu item
10 | Display of Chosen I:E Ratio | YES - ticker
10B | I:E at least 1:1 1:2 1:3 | YES 1:1,2,3,4
11 | Display of Chosen Peak Pressure Limit | YES - ticker
12 | Display of Chosen Flow Limits(upper lower or otherwise) | YES – center in ticker
13 | Display of airway pressure observed | YES - 1st line of display
13B | Display of PEEP | Chosen – ticker Observed – see 1st line
14 | Display of flow measured | Volume displayed first line
15 | Low pressure alarm | YES – checked
16 | High Pressure alarm | YES – checked
17 | Stop inspiration at high pressure alarm | YES – checked
18 | Open expiratory valve at high pressure alarm | YES – verified
19 | Alarm for low flow volume | YES - verified
20 | Alarm for high flow volume | YES - verified
21-29 Reserved
30 | Alarm Temporary Silence | YES – initiate menu
31 | Inspiratory Pause Enable | YES - verified
32 | Inspiratory Pause Disable | YES - verified
33 | Assist Ventilation Enable | YES (when insp pause off)
34 | Assist Ventilation Disable | YES (when insp pause ON)
35 | Trigger for Assist Ventilation | Adjustable false triggered at 3cmworked at 4 cmmax value 15 below set peep value
36 | Delay from trigger to effective inspiratory assistance | Virtually instantaneous
40 | Failure if button held down | NO
41 | Outcome of random simultaneous button presses | Expected actions
42 | Outcome of pulling power | (no battery on my prototype; previously checked, no impact)
43 | Outcome of pulling BMP280 clock line | Switches into open-loop mode with tone on each inspiration.
44 | Outcome of pulling BMP280 data line | On 1st try – inspiration continued without stopping –system “hung”. Had to de-powerRepeated two more times, coutd not repeat. System switches to open loop mode with short dit at start of each breath. | We will be dependent on the mechanical overpressure if the I2C bus failure causes the processor to hang.....There is nothing code can do....when the processor is hung. Until the watchdog timer would intervene and the pressure would have to be controlled by mechanical means until then. This is the ONLY time I have ever seen this in many many tests (estimate >20) but it did happen!
45 | Outcome of pulling BMP280 Vin line | Switched to open loop mode with beep on each inspiration
46 | Function of ventilator with missing BMP280glue (cold start) | Open loop mode with beep on each inspiration | Note PEEP isn’t possibe.
47 | Technique to re-enable BMP280 | Menu operation, results in dit-dit-DASH to notify and screen display. Then restart Vent (menu operation)
48 | Outcome of attempting to re-enable BMP | Works flawlessly
49-50 Reserved
50 | Measured RR @ setting 10 | 10.0 | While providing 10 cm peep
51 | Measured RR @ setting 30 | 30.0 | While providing 10 cm peep
52 | Measure of idle time of processor | (Done in previous tests: making four total I2c calls, the fast portion of expiratory limb is doing all four in approximately 23 milliseconds.
53 | Active PEEP
54 | Assist Vent

## Open Source Ventilator Project

- Open Source Ventilator Project
- marshallrawson@ufl.edu
- MarshallRawson (https://github.com/MarshallRawson)

This is an open source ventilator project made by students and retirees at the University of Florida in their spare time.

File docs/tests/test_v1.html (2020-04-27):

Open Source Ventilator Project (http://127.0.0.1:4000/Open_Source_Ventilator/)

This is a black testing report we host for developers to fill out when they are proposing updating the code on master.

# Testing Report

Date | Version | Revision
4/16/202 | Draft V1.0 | Original G. Gibby

Date: 4/21/2020

Test Evaluator: Gordon Gib

Item | Description | Result | Comment
1. | Software being evaluated. Include version, author, date, | VentcodeJack Edits.ino Ventilator/Ashar1.0/MyLocalCopyPurdum0418wFarhanUI/FarhanO420
2 | Compile outcome | (#define prints turned off) + non sig warning diffpressure | only one non-meaningful warning left!
3 | % of program space | 64%
4 | % of dynamic memory | 71%
5 | Zero’ing of airway pressure sensor | Come up = I2C disabled -> Reset -> works | Investigate
6 | Zero’ing of flow measurement system | Yes (insensitive analog 2kPa reading 48-84 mL)
7 | Ability to re-zero during later operation | Yes – “Reset I2C”
8 | Protection from accidentally turning Ventilator OFF | Requires 7 button presses | Better if it CONFIRMED
9 | Display of Chosen Respiratory Rate | (Missing from ticker!)(an oversight....) | <- Please fix!(shows in adjustment)
9B | RR selectable | Yes (by ONES)
10 | Display of Chosen I:E Ratio | Yes (ticker) of Ticker Setting
10B | I:E at least 1:1 1:2 1:3 | Yes 1:1 1:2 1:3 1:4 Yes ticker of setting
11 | Display of Chosen Peak Pressure Limit | Yes – ticker & setting
12 | Display of Chosen Flow Limits(upper lower or otherwise) | Yes – ticker & setting
13 | Display of airway pressure observed | Yes both peak (latch) and expiration (non latch)
13B | Display of PEEP | Discern from exp press display
14 | Display of flow measured | Yes
15 | Low pressure alarm | Yes – Flashes ***LO PR**
16 | High Pressure alarm | Yes – Flashes ***HI PR**
17 | Stop inspiration at high pressure alarm | Yes – interrupts inspiration | Appear total ~ 100 mSec
18 | Open expiratory valve at high pressure alarm | Yes
19 | Alarm for low flow volume | Yes – Flashes ***LO VO**
20 | Alarm for high flow volume | Yes – Flashes ***HI VO**
21-29 Reserved
30 | Alarm Temporary Silence | No (RESET ALARMS only)
31 | Inspiratory Pause Enable | Yes (menu)
32 | Inspiratory Pause Disable | Yes (menu)
33 | Assist Ventilation Enable | Whenever NOT in insp. pause
34 | Assist Ventilation Disable | Put into insp. pause
35 | Trigger for Assist Ventilation | (-5 below set peep from software—not tested here)
36 | Delay from trigger to effective inspiratory assistance | Almost instantaneous
40 | Failure if button held down | NONE
41 | Outcome of random simultaneous button presses | Expected action
42 | Outcome of pulling power | Continues on battery
43 | Outcome of pulling BMP280 clock line | Becomes time cycled simple vent – shows 0 pressure 0 flow | Why does it show zero flow??
44 | Outcome of pulling BMP280 data line | Not tested | Not tested
45 | Outcome of pulling BMP280 Vin line | Not tested
46 | Function of ventilator with missing BMP280glue (cold start) | Had to formally tell it to start after reloading software connecting serial port. Cold startt BMP would not start – something about the serial port made it start?? | Check for serial port issues.
47 | Technique to re-enable BMP280 | Menu selection – patience – then select START | Must wait until reset showsup again on the line – then exit the re-enable and go to ventilator → set ON. Restarts perfectlly.’
48 | Outcome of attempting to re-enable BMP | Good – it re-zeroes and restarts.
49-50 Reserved
50 | Measured RR @ setting 10 | 10
51 | Measured RR @ setting 30 | 30 | Note: tested with Peep 10
52 | Measure of idle time of processor | Previously done)
53 | Active PEEP | Yes
54 | Assist Vent | Yes

## Open Source Ventilator Project

- Open Source Ventilator Project
- marshallrawson@ufl.edu
- MarshallRawson (https://github.com/MarshallRawson)

This is an open source ventilator project made by students and retirees at the University of Florida in their spare time.

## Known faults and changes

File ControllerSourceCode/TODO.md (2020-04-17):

## Thanks for volunteering in collaborating with this project.

There is a playlist with some videos about this code:

[https://www.youtube.com/watch?v=gKr-EH8vHxM&list=PLtBsFN3o4c54h5fr7lDnGuZhvKIA5Fhd3](https://www.youtube.com/watch?v=gKr-EH8vHxM&list=PLtBsFN3o4c54h5fr7lDnGuZhvKIA5Fhd3)

I did not have a chance yet to document it as we are very very busy these days.

Following are things in my TODO list (other than adding features):

*  :white_check_mark:[DONE] Prevent the “params" array structure to use RAM. There is a huge limitation in this processor where even when you define a “const whatever” it allocates program space as well as a  DUPLICATION of it in RAM. I can give you more background about it  in case you decide to start wit that.

* same idea than above for alarms's array in alarm.cpp: use PROMEM to save RAM.

* Hack the Bootloader to pass the content of the watchdog register information. Actually the boot loader makes this register available in the processor R2. But the boot loader resets the flag that we are interesting in before calling out App. Again, I can give you more details and there are already boot loaders with this hack.

* Non initialized variable in RAM: we would like to have some variable stored in RAM that would survive resets. However, just by following the suggested procedures,  it does not work. My guess is that the linker scripts were changed in the toolchain and need to be hacked.

* Optimize RAM as much as we can: check all bool’s and int’s and replace by int8_t declarations. this is to save RAM.

* separate the config for each board in a dedicated header file (board_xxxx.h). config.h will just include a single board_xxxx.h file.

* get rid of most (if not all) floating point computations.

* better abstract pressure sensor options (NXP 7002 and BMP280)

* create a separated "discover" program to help guys integrating stepper motor with their mechanism: allow operator to move motor using buttons to extract parameters to be read and later written in the real controller code.

We may have more features coming as well.

At this point, while we do not have PCB's available for everyone, you would need a Arduino Nano to test your code. Even better if you have the same LCD we are using.

Regards,
Marcelo

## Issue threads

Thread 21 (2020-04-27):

### ISSUE TITLE
Parts list

### ISSUE THREAD

**Issue by wuhland** [CSSALTlab/Open_Source_Ventilator#21]
Is there a parts list available? If so it is not easy to find.

**Comment by MarshallRawson** [comment]
Take a look at out [operator's manual](https://cssaltlab.github.io/Open_Source_Ventilator/docs/OperatorsManual/manual.html) , it has the parts list for an operator's perspective. We are currently working on better docs, and a parts list will be coming soon. :)

**Comment by MarshallRawson** [comment]
see [our assembly instructions](https://cssaltlab.github.io/Open_Source_Ventilator/docs/electronics/assembly_instructions.html)

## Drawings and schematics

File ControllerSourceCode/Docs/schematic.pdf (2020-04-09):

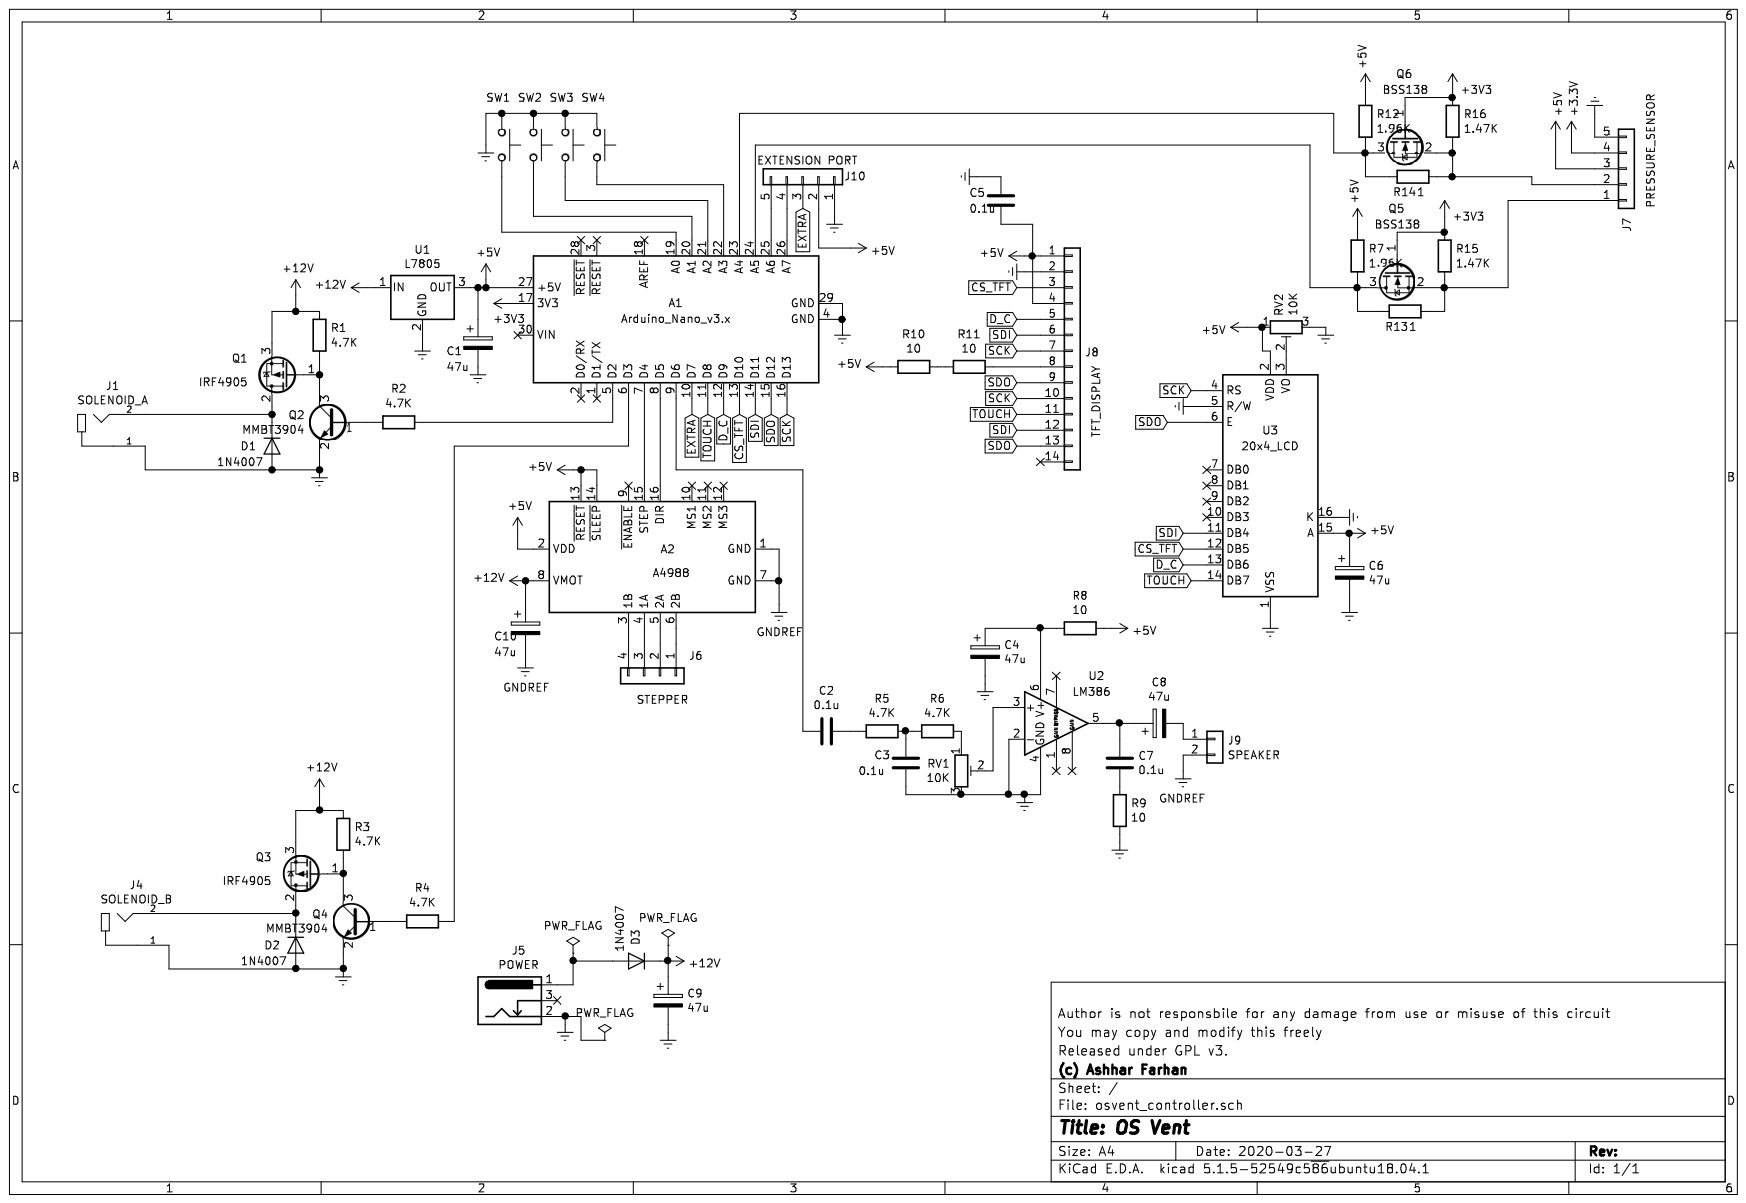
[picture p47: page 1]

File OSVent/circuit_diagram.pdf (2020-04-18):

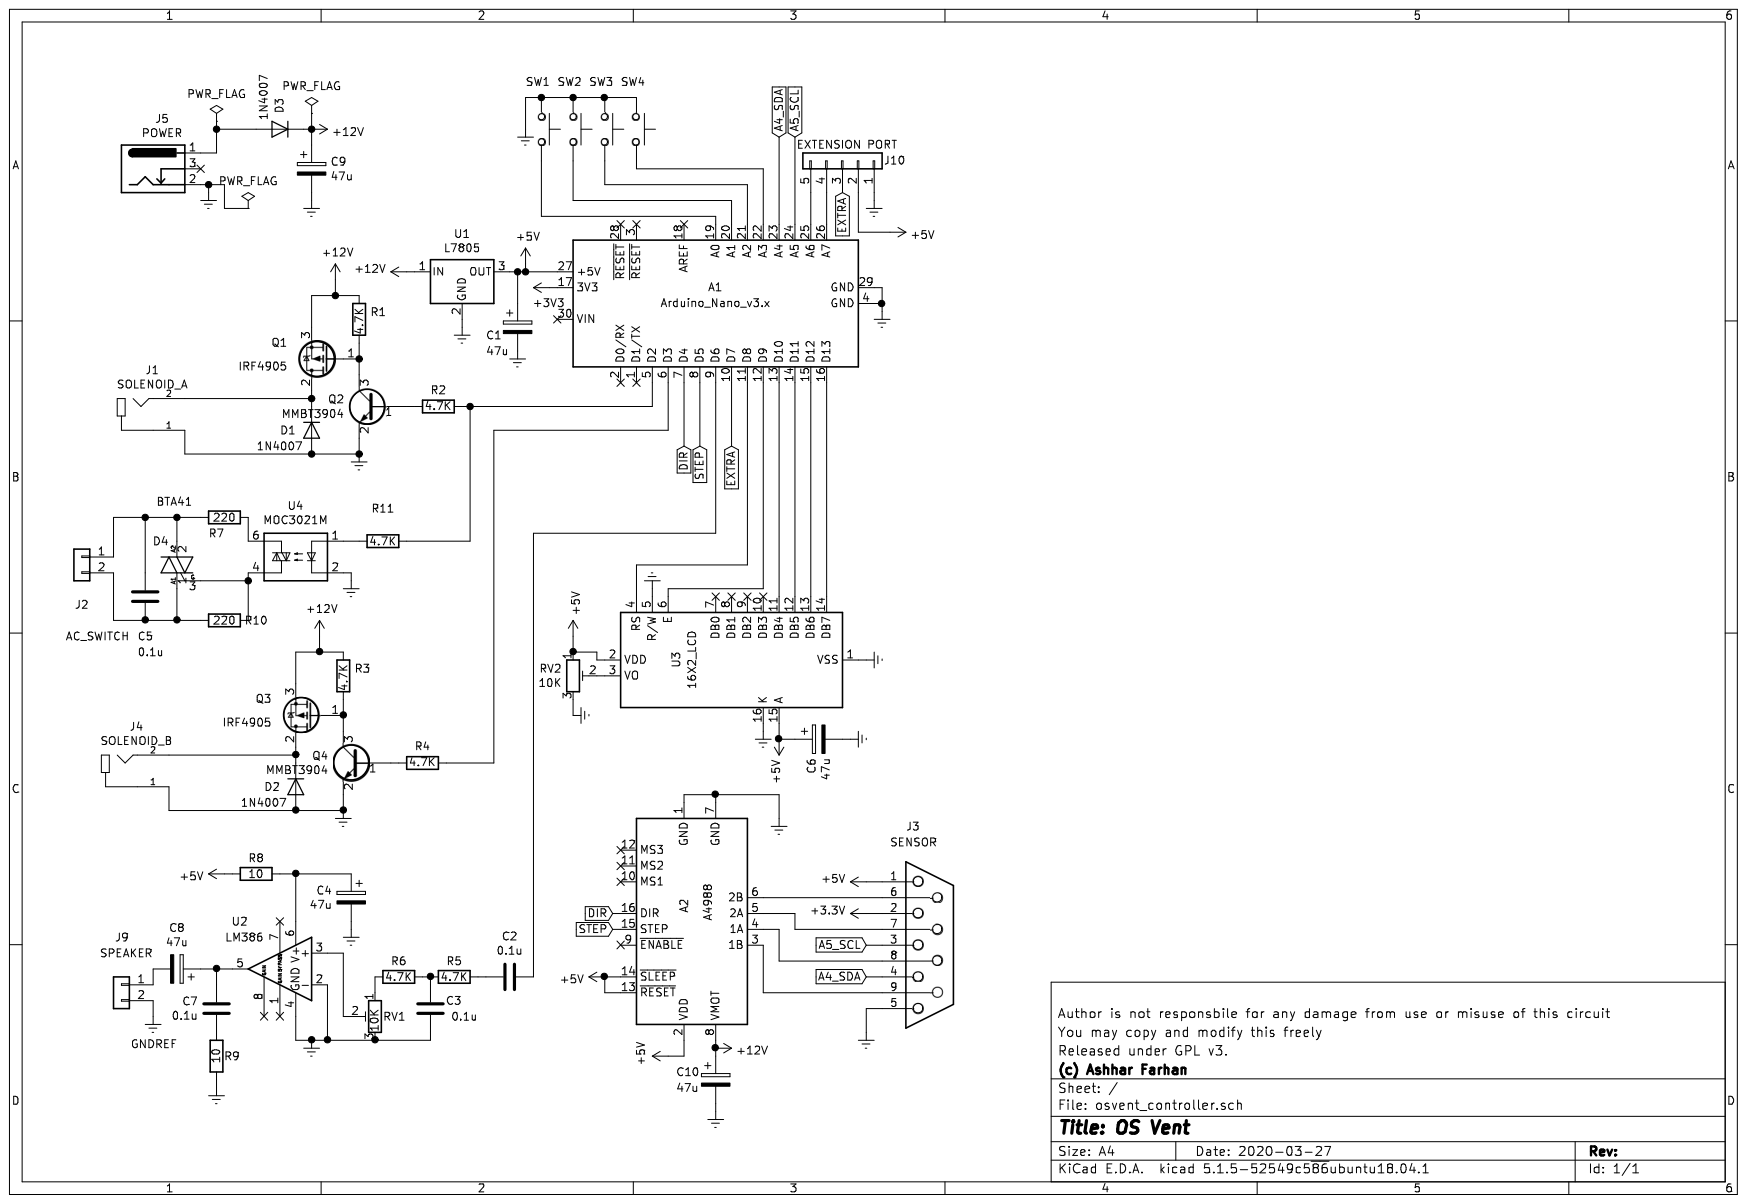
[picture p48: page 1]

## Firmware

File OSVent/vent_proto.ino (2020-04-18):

#include <Wire.h>
#include <EEPROM.h>
#include <BMP180I2C.h>
#include <avr/wdt.h>

#include "nano_gui.h"
#include "vent.h"
#define I2C_ADDRESS 0x77

//create an BMP180 object using the I2C interface
BMP180I2C bmp180(I2C_ADDRESS);
#define MOTOR_A 2
#define MOTOR_B 3

int use_tft = 0;

#define EEPROM_VENT_ON  48
#define EEPROM_BPM      52
#define EEPROM_PRESSURE 56
#define EEPROM_IERATIO  60

int beats_per_minute = 10;
int ie_ratio = 1; //this is the denominator
int vent_pressure = 160; //this is in mm
int vent_temperature;
int vent_running = 1;
int pressure_sensor_present = 0;

//draw the graph
int bargraph[MAX_PHASES];
int current_phase = 0;
long next_slice = 0;
int is_pressure_on = 0;
long  atmospheric_pressure = 0;
int current_pressure = 0;
long pressure_total = 0;
long pressure_peak = 0;

byte automatic_pressure_level = false;

void checkCAT(){
  
}

void save_settings(){
  EEPROM.put(EEPROM_VENT_ON, vent_running);
  EEPROM.put(EEPROM_BPM, beats_per_minute);
  EEPROM.put(EEPROM_PRESSURE, vent_pressure);
  EEPROM.put(EEPROM_IERATIO, ie_ratio);    
}

void load_settings(){
  EEPROM.get(EEPROM_VENT_ON, vent_running);
  EEPROM.get(EEPROM_BPM, beats_per_minute);
  EEPROM.get(EEPROM_PRESSURE, vent_pressure);
  EEPROM.get(EEPROM_IERATIO, ie_ratio);
  if (vent_running != 1){
    Serial.println("*default vent off");
    vent_running = 0;
  }
  if (beats_per_minute < 0 || beats_per_minute > 30){
    Serial.println("*default 10/bpm");
    beats_per_minute = 10;
  }
  if (vent_pressure < 50 || vent_pressure > 300){
    vent_pressure = 150;
    Serial.println("*default pressure 15 cm");    
  }
  if (ie_ratio < 1 || ie_ratio > 4){
    Serial.println("*default I/E ration = 1:1");
    ie_ratio = 1;   
  }
}

void set_status(char *text){
  if (use_tft)
    displayText(text, 0,0,320,78, DISPLAY_GREEN, DISPLAY_BLACK, DISPLAY_BLACK);
  else
    lcd_status(text);
}

void show_message(char *text){
  if (use_tft)
    displayText(text, 0,0,320,78, DISPLAY_GREEN, DISPLAY_BLACK, DISPLAY_BLACK);
  else
    lcd_message(text);
  Serial.println(text);
}

//returns the absolute pressure in mmH20
//based on the formula at https://www.convertunits.com/from/mmH2O/to/Pa
long measure_pressure(){   
   
  //start a temperature measurement
  if (!bmp180.measureTemperature())
  {
    show_message("No Sensor");
    return;
  }

  //wait for the measurement to finish. proceed as soon as hasValue() returned true. 
  do
  {
    delay(0);
  } while (!bmp180.hasValue());
  vent_temperature = (int)bmp180.getTemperature();
  Serial.println(vent_temperature);

  //start a pressure measurement. pressure measurements depend on temperature measurement, you should only start a pressure 
  //measurement immediately after a temperature measurement. 
  if (!bmp180.measurePressure()){
    Serial.println("Sensor Err2");
    return;
  }

  //wait for the measurement to finish. proceed as soon as hasValue() returned true. 
  do{
    delay(0);
  } while (!bmp180.hasValue());

  long p = (long)bmp180.getPressure();  
  return ((102l * p)/1000l);
}

void measure_atmospheric_pressure(){

  //if pressure is on, turn it off and wait for 8 seconds for the lungs and compressor to deflate
  if (is_pressure_on){
    pressure_off();
    delay(8000);
  }
  //now calibrate for 5 seconds
  atmospheric_pressure = 0;
  for (int i = 0; i < 10; i++){
    atmospheric_pressure += measure_pressure();
    delay(200);
  }
  //now take the average
  atmospheric_pressure /= 10;
}

int loop_count = 0;

void pressure_on(){
  if (is_pressure_on == 0){
    digitalWrite(MOTOR_A, HIGH);
    digitalWrite(MOTOR_B, LOW);
    is_pressure_on = 1;
    Serial.print(millis());
    Serial.println(": on");
  }
}

void pressure_off(){
  if (is_pressure_on != 0){
    digitalWrite(MOTOR_A, LOW);
    digitalWrite(MOTOR_B, HIGH);
    is_pressure_on = 0;  
    Serial.print(millis());
    Serial.println(": off");
  }
}


/*
 * This has to be tweaked
 */
void check_pressure_limits(){
  //check for over-pressure
  if (current_pressure > (vent_pressure * 15)/10){
    alarm(ALARM_FAST);
    set_status("HI");
  }
    
  if (current_phase == 0){
    pressure_total = 0;
  }

  //check only if the current phase is ending
  if (current_phase != MAX_PHASES - 1)
    return;
  if ((pressure_total * ie_ratio * 2)/MAX_PHASES < vent_pressure ){
    alarm(ALARM_SLOW);
    set_status("LO");
  }     //tujrn off only if the peak pressure isn't too much either
  else if (pressure_peak < (vent_pressure * 12)/10){
    alarm(ALARM_OFF);
    set_status("ON");
  }
  
}

void setup_watchdog(void){
  cli();
  wdt_reset();
  /*
  WDTCSR configuration:
  WDIE = 1: Interrupt Enable
  WDE = 1 :Reset Enable
  See table for time-out variations:
  WDP3 = 0 :For 1000ms Time-out
  WDP2 = 1 :For 1000ms Time-out
  WDP1 = 1 :For 1000ms Time-out
  WDP0 = 0 :For 1000ms Time-out
  */
  // Enter Watchdog Configuration mode:
  WDTCSR |= (1<<WDCE) | (1<<WDE);
  // Set Watchdog settings:
  WDTCSR =(1<<WDIE) | (1<<WDE) |(1<<WDP3) | (0<<WDP2) | (0<<WDP1) |(1<<WDP0);
  sei();
}


void vent_slice(){
  long now, p;

  if (!vent_running){
    alarm(ALARM_OFF);
    show_message(">>OSVent Ready<<");
    return;
  }

  now = millis();
  if (next_slice > now)
    return;

  int cut_off = MAX_PHASES - (MAX_PHASES * (ie_ratio))/(ie_ratio + 1);

  check_pressure_limits();
    
  //we move to the next slice
  if (current_phase < cut_off)
    pressure_on();
  if (current_phase > cut_off)
    pressure_off();
    
  next_slice = now + 60000l / ((long)beats_per_minute * (long)MAX_PHASES);

  p = measure_pressure();  
  bargraph[current_phase] = (int)(p - atmospheric_pressure);
  current_pressure = bargraph[current_phase];
  pressure_total += current_pressure;
  if (use_tft)
    tft_graph_update();
  else 
    lcd_graph_update();
  current_phase++;
  
  if (current_phase >= MAX_PHASES){
   if (use_tft)
      tft_graph_clear();
    else
      lcd_graph_clear();
    current_phase = 0;    
  }
 // Serial.print("tot:");
 // Serial.println(pressure_total);
}

void  vent_start(){
  current_phase = 0;
  vent_running = 1;
}

//at times the motor/valve maybe stuck, try turning it off twice
void vent_abort(){
  pressure_off();
  current_phase = 0;
  vent_running = 0;
  delay(200);
  pressure_off();
}
void vent_init(){

  //premptively give this error
  show_message("No Sensor");

  //begin() initializes the interface, checks the sensor ID and reads the calibration parameters.  
  if (!bmp180.begin()){
    pressure_sensor_present = 0;
    while (1);
  }

  //reset sensor to default parameters.
  bmp180.resetToDefaults();

  //enable ultra high resolution mode for pressure measurements
  bmp180.setSamplingMode(BMP180MI::MODE_UHR);

  show_message("Sensor OK");
  measure_atmospheric_pressure();
  show_message("Ready");  
}

void setup() {
  // put your setup code here, to run once:

  setup_watchdog();

  pinMode(MOTOR_A, OUTPUT);
  pinMode(MOTOR_B, OUTPUT);
  digitalWrite(MOTOR_A, LOW);
  digitalWrite(MOTOR_B, LOW);
  
  Serial.begin(9600);
  while (!Serial);

  load_settings();

  Wire.begin();

  if (use_tft)
    tft_init();
  else
    lcd_init(1602);  


  vent_init();
  //setupTouch();
  Serial.println("Setup done");
}

void loop() {
  vent_slice();
  alarm_slice();
  wdt_reset();
  if (use_tft)
    tft_slice();
  else
    lcd_slice();
  //Serial.println(measure_pressure());
  delay(100);
}

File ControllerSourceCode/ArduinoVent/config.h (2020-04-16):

#ifndef CONFIG_H
#define CONFIG_H

/*************************************************************
 * Open Ventilator
 * Copyright (C) 2020 - Marcelo Varanda
 *
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
 **************************************************************
*/

/*======================================
  =                                    =
  =             Language               =
  =                                    =
  ======================================
 */

#define LANGUAGE_EN_US      1           // English
#define LANGUAGE_PT_BR      0           // Portuguese

//#define NO_ALARM_SOUND // development only... must be commente out for production
#ifdef NO_ALARM_SOUND
  #warning "Alarm Sound is MUTED"
#endif

/*======================================
  =                                    =
  =          Hardware Mapping          =
  =                                    =
  ======================================
 */

#define DEBUG_SERIAL_LOGS // MUST be commented out for production. Also a hack is needed to decrease buffers in HardwareSerial.h

#ifndef VENTSIM
  #define WATCHDOG_ENABLE  // to disable watchdog comment out this line
#else
enum {A0, A1, A2, A3, A4, A5, A6, A7};
#endif


/*************************************************
 * 
 *         B O A R D   S E L E C T I O N
 *                            
 *************************************************
 */
// Note: also add boards defined here in below's "Board check selection" just in case.
#define       HW_VERSION_CSSALT_PROTO_01        1  // CSSALT Board ref 1 (Arduino Nano)
#define       HW_VERSION_CSSALT_PROTO_02        0  // CSSALT Board ref 1 (Arduino Nano) 20x4 LCD and Motor
#define       HW_VERSION_MV_01                  0  // Marcelo's prototype (Arduino Uno)
#define       HW_VERSION_MV_SIMULATOR           0
//-------------------------------------------------





/*
                ***********************************************
                *                                             *
                *                     BOARDS                  *
                *                                             *
                ***********************************************
*/

#if (HW_VERSION_CSSALT_PROTO_01 == 1)
/******************************************
 * 
 *         Hardware prototype PCB rev 01
 *                  Arduino Nano
 *                  
 ******************************************
 */


//------------ Input Keys ---------------

#define KEY_DECREMENT_PIN       A0
#define KEY_INCREMENT_PIN       A1
#define KEY_SET_PIN             A3

//------------ Output Valves -----------
#define VALVE_IN_ACTIVE_LOW
//#define VALVE_OUT_ACTIVE_LOW

#define VALVE_IN_PIN            2 // D2
#define VALVE_OUT_PIN           3 // D3

#ifndef BLUETOOTH_ENABLE
  #define MONITOR_LED_PIN LED_BUILTIN
#else
  #define MONITOR_LED_PIN       13
#endif

#define  ALARM_SOUND_PIN        6  // D6

//----------- PRESSURE_SENSOR ------------
#define PRESSURE_SENSOR_PIN     A7

#define USE_Mpxv7002DP_PRESSURE_SENSOR  0
#define USE_BMP280_PRESSURE_SENSOR      1

// BMP sensor connetcted to   SDA -> A4
//                            SCL -> A5

//---------- FLOW SENSOR ----------
#define USE_Mpxv7002DP_FLOW_SENSOR      1
#define FLOW_SENSOR_PIN         A6

//--------- LCD Num Rows ----------
// Default
#define LCD_CFG_20_COLS  0
#define LCD_CFG_16_COLS  1

#define LCD_CFG_2_ROWS  1
#define LCD_CFG_4_ROWS  0

// Parallel LCD
#define LCD_CFG_D7              8   // Connector Pin 11 - Digital 8
#define LCD_CFG_D6              9   // Connector Pin 12 - Digital9
#define LCD_CFG_D5              10  // Connector Pin 13 - Digital10
#define LCD_CFG_D4              11  // Connector Pin 14 - Digital11
#define LCD_CFG_E               12  // Connector Pin 15 - Digital12
#define LCD_CFG_RS              13  // Connector Pin 16 - Digital13

// stepper motor
//#define   STEPPER_MOTOR_STEP_PIN   4 // D4. also, if this is undefined (commented) the motor function if disabled
//#define   STEPPER_MOTOR_DIR_PIN    5 // D5
//#define   STEPPER_MOTOR_EOC_PIN    // TBD... Enf-Of-Course sensor (switch) active low.
                                        
//#define   STEPPER_MOTOR_INVERT_DIR  // uncoment/comment this line according to your mechanic orientation

/* LiquidCrystal     (rs, enable, d4, d5, d6, d7)
   LiquidCrystal lcd( LCD_CFG_RS, LCD_CFG_E, LCD_CFG_D4, LCD_CFG_D5, LCD_CFG_D6, LCD_CFG_D7);
*/

#elif (HW_VERSION_CSSALT_PROTO_02 == 1)
/******************************************
 * 
 *         Hardware prototype PCB rev 01
 *                  Arduino Nano
 *                  
 ******************************************
 */
//------------ Input Keys ---------------

#define KEY_DECREMENT_PIN       A0
#define KEY_INCREMENT_PIN       A1
#define KEY_SET_PIN             A3

//------------ Output Valves -----------
#define VALVE_IN_ACTIVE_LOW

#define VALVE_IN_PIN            2 // D2
#define VALVE_OUT_PIN           3 // D3

#ifndef BLUETOOTH_ENABLE
  #define MONITOR_LED_PIN LED_BUILTIN
#else
  #define MONITOR_LED_PIN       13
#endif

#define  ALARM_SOUND_PIN        6  // D6

//----------- PRESSURE_SENSOR ------------
#define PRESSURE_SENSOR_PIN     A7

#define USE_Mpxv7002DP_PRESSURE_SENSOR  0
#define USE_BMP280_PRESSURE_SENSOR      1

// BMP sensor connetcted to   SDA -> A4
//                            SCL -> A5

//---------- FLOW SENSOR ----------
#define USE_Mpxv7002DP_FLOW_SENSOR      1
#define FLOW_SENSOR_PIN         A6

//--------- LCD Num Rows ----------
// Default
#define LCD_CFG_20_COLS  1
#define LCD_CFG_16_COLS  0

#define LCD_CFG_2_ROWS  0
#define LCD_CFG_4_ROWS  1

// Parallel LCD
#define LCD_CFG_D7              8   // Connector Pin 11 - Digital 8
#define LCD_CFG_D6              9   // Connector Pin 12 - Digital9
#define LCD_CFG_D5              10  // Connector Pin 13 - Digital10
#define LCD_CFG_D4              11  // Connector Pin 14 - Digital11
#define LCD_CFG_E               12  // Connector Pin 15 - Digital12
#define LCD_CFG_RS              13  // Connector Pin 16 - Digital13

// stepper motor
#define   STEPPER_MOTOR_STEP_PIN   4 // D4. also, if this is undefined (commented) the motor function if disabled
#define   STEPPER_MOTOR_DIR_PIN    5 // D5
//#define   STEPPER_MOTOR_EOC_PIN    // TBD... Enf-Of-Course sensor (switch) active low.
#define   STEPPER_MOTOR_INVERT_DIR  // uncoment/comment this line according to your mechanic orientation

//-------------------------------------------------------------------

#elif (HW_VERSION_MV_01 == 1)
/******************************************
 * 
 *         Hardware prototype Marcelo 01
 *                  Arduino Uno
 *                  
 ******************************************
 */
//------------ Input Keys ---------------

#define KEY_DECREMENT_PIN       3
#define KEY_INCREMENT_PIN       4
#define KEY_SET_PIN             5

#define  ALARM_SOUND_PIN        8  // D8

//------------ Output Valves -----------
#define VALVE_IN_ACTIVE_LOW

#define VALVE_IN_PIN            6
#define VALVE_OUT_PIN           7

#ifndef BLUETOOTH_ENABLE
  #define MONITOR_LED_PIN LED_BUILTIN
#else
  #define MONITOR_LED_PIN       13
#endif

//----------- PRESSURE_SENSOR ------------
#define PRESSURE_SENSOR_PIN     A7
#define FLOW_SENSOR_PIN         A0

//--------- LCD Num Rows ----------
// Default
#define LCD_CFG_I2C
#define LCD_CFG_20_COLS  0
#define LCD_CFG_16_COLS  1

#define LCD_CFG_2_ROWS  1
#define LCD_CFG_4_ROWS  0
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

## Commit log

2020-03-22 Adding directory structure for both Arduino and Simulator projects.
2020-03-22 Arduino and Qt common files concept working :-). Implemented millis for Qt.
2020-03-22 implemented basic LCD functions for both Arduino and Sim.
2020-03-23 Add real keys and valve I/O's
2020-03-25 Enable Watchdog. Monitor LED have 3 speeds. The idea was to blink fast when recovering from watchdog. However, bootloader hack would be needed to get access to saved MCUSR register (need to check WDR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
2020-03-26 Update README.md
    Add prototype picture.
2020-03-31 add printf like log (limited to 64 bytes)
2020-04-01 Adding HW mappint to CSSALT prototype rev1. LCD still with a bug (no end of line) but showing expected characters
2020-04-02 add pressure sensor sampler.
2020-04-02 fix pressure conversion to IncH2O.
2020-04-02 Add pressure item to be displayed.
2020-04-04 Low and high pressure alarms working with analog sensor. Thresholds hardcoded to 3 and 35 InchH2O.
2020-04-05 added analog pressure sensor simulation for VentSim.
2020-04-05 Add simulator as a board option in config file.
2020-04-06 Switch back to UF PCB (by mistake I had pushed Simulator selected)
2020-04-08 Add documentation about A4988: stepper motor driver
2020-04-09 Adding schematic for Ashhar rev.1 board and A4988 ndatasheet
2020-04-10 Add stepper motor test
    By now stepper just move 5 laps in both directions upon start up.
2020-04-12 Add another test board with motor on
2020-04-12 Create room for Flow sensor (not tested)
2020-04-12 Add properties for Flow and pressure
2020-04-12 Added fast calibration
2020-04-13 select board.
2020-04-14 Add fast calibration to breather motor
2020-04-14 fix missing stubs for other board
2020-04-14 Fix Marcelo's board config.
2020-04-16 Add proper calibration for pressure sensor
    - breather startup waits 4 seconds to grab pressure reference
    - Fast calibration fully implemented
    - valve commands using open/close wording.
    - valves can independent be reverse in config.h
    - remove unnecessary BMP readings (save time and space)
2020-04-17 Fix Simulator and added a Valve test tool
    Video about the Valve test tool:
    https://youtu.be/2kokoPZn_B4
2020-04-18 Doxygen sample for commenting a file
2020-04-27 Added Assembley manual
2020-04-27 DOCS: added assembly instructions to home page
2020-06-17 Update README.md
    Added quick note for including sensor libraries.
2021-02-08 Retroactively added features from v135 to expiratory side flow meter set up

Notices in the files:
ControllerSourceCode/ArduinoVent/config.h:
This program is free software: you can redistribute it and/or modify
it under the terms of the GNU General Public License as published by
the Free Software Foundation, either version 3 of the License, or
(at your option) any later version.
